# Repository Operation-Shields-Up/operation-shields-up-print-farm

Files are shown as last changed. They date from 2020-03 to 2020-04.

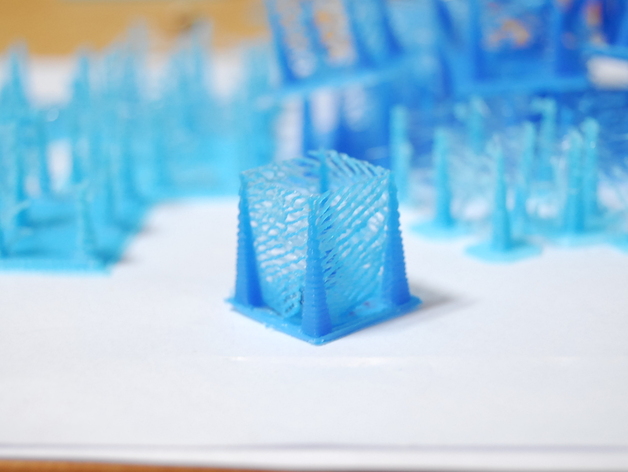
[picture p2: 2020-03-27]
models/calibration/Retraction_test_/images/cDSC_0050_preview_featured.jpg

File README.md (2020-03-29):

# Operation Shields UP

## GUIDES

- [Extrusion multiplier calibration](https://help.prusa3d.com/en/article/extrusion-multiplier-calibration_2257)

## FAQ

Q: What type of filament can I use?

A: We prefer PETG but will accept PLA.

Q: What settings should I use when I slice the models?

A: We are using a .2 mm layer height and a infill of 45% or more.

Q: Will the models change?

A: Likely, please follow the repo and we will update the files as we adopt new versions.
   We are actively working with PRUSA helping to vet the designs and integrate them with 
   our process and other components.

Q: How do I get in contact with you?

A: Reach us through our website [https://www.opshieldsup.org](https://www.opshieldsup.org)

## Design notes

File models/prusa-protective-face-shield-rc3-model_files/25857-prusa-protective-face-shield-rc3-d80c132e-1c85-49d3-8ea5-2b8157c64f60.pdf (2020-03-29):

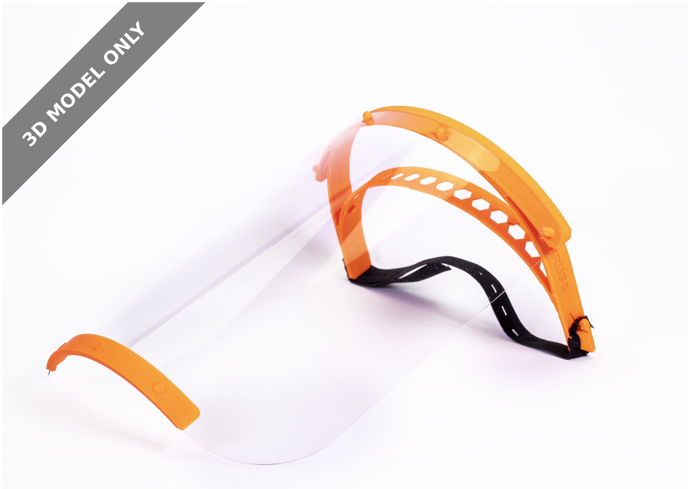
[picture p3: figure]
3D MODEL ONLY

## Summary

A prototype face shield that we developed. In three days, we went through dozens of prototypes and two verifications with the Czech Ministry of Health.

Check this print (https://www.prusaprinters.org/prints/27267) for 2 and 4 stack versions.

Version RC3 changelog Changes from RC2:

Removed hexagonal holes for faster printing speeds
With faster printing we use on our farm, some pieces had sharp points and based on testing, the venting is not needed as much Several optimizations for stack printing
New print files with 4 headbands stacked (https://www.prusaprinters.org/prints/27267) on top of each other Stacking headbands is a great idea by the community, especially useful for overnight printing

Prusa Research (https://www.prusaprinters.org/social/16/prints)

## Prusa Protective Face Shield - RC3

VIEW IN BROWSER (https://www.prusaprinters.org/prints/25857-prusa-protective-face-shield-rc3)

updated 27. 3. 2020 | published 26. 3. 2020

•
◦

•
•
◦

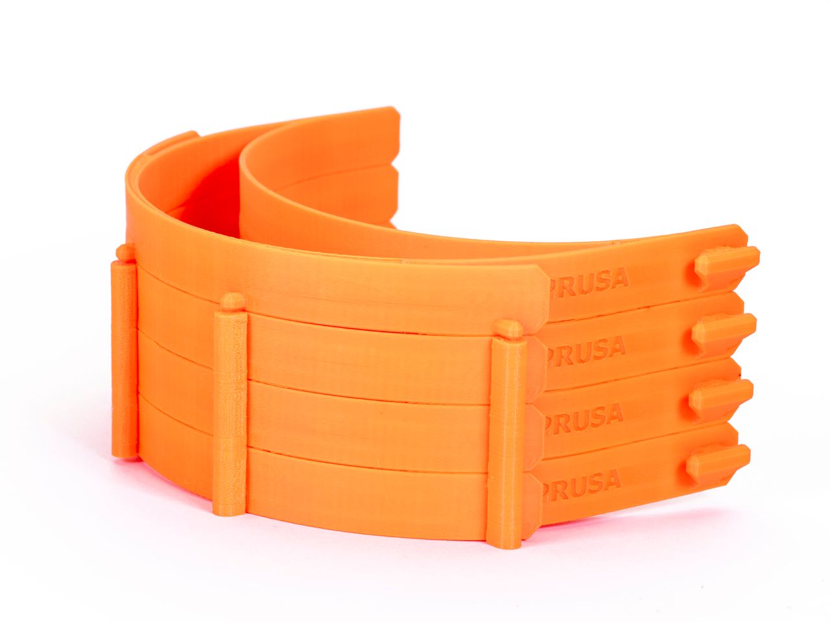
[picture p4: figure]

Version RC2 Changes from RC1:

Increased wall thickness (slightly stiffer and more durable)
Inner wall from 1.5 mm to 2 mm
Outer wall from 2 mm to 2.5 mm
The headband is no longer printed compressed - Lower pressure on the temple
The visor was moved further away from the forehead - This allows a better fit over bigger respirators and protective goggles
The printed part now has an extension for the visor (the visor curves less than the headband).

For now, both RC1 and RC2 versions are relevant. RC1 lets you fit more printed parts on a single print bed. However, if maximum yield isn’t the priority, RC2 provides slightly better protection and is more comfortable to

•
◦
◦
•

•

•

wear.

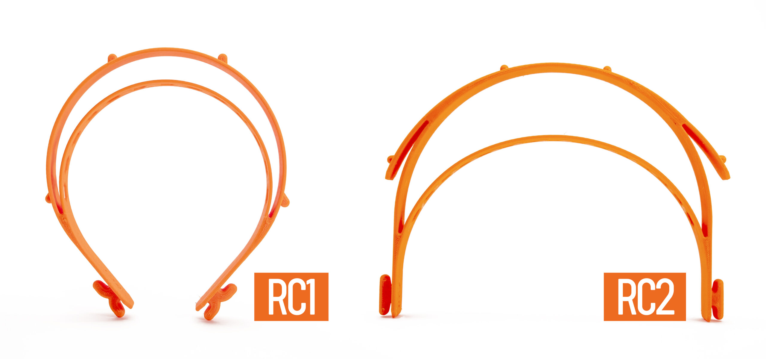
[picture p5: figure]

If you want to manufacture shields for others PLEASE READ THIS CAREFULLY

Act as if you were infected by the COVID-19 virus. Wear a face mask and a fresh pair of gloves when collecting each batch of printed parts. Store the parts immediately in a sealable bag.
Talk with whoever you’re making the shields for, let them know about your manufacturing environment
There is still debate about how long the virus survives on plastic, but most sources mention 2-3 days. That means that by letting the packed face shields sit for 2-3 days before distributing them, you’ll greatly reduce risk of transmission
Do not store the entire stock in one place, minimize the risk of cross contamination

More information: https://blog.prusaprinters.org/from-design-to-mass-3d-printing-of-medical-shields-in-three-days/ (https://blog.prusaprinters.org/from-design-to-mass-3d-printing-of-medical-shields-in-three-days/)

How to STERILIZE the face shields Sterilization guide (https://help.prusa3d.com/en/article/prusa-face-shield-disinfection_125457) We have tests with live COVID running to verify as many of these sterilization methods as possible.

Assembly manual: English version (https://manual.prusa3d.com/Guide/Prusa+Face+Shield/1527) English Community version using a laminating foil (https://manual.prusa3d.com/Guide/Assembling+the+Prusa+Face+Shield+-+community+version/1528#s41280) Czech version (https://manual.prusa3d.com/Guide/Prusa+Oblicejovy+Stit/1526)

Video:

"https://www.youtube.com/embed/pP7z3iw76GA"

Rubber band You can either use a thicker one and make a hole in it at each end (make at least 10 mm cut) or use a thin one and tie it to both ends of the shield.

•

•

•

•

Model Files (.stl, .3mf, .obj, .amf) | DOWNLOAD ALL FILES (https://www.prusaprinters.org/prints/25857-prusa-protective-face-shield-rc3/files)

354.1 KB
updated 26. 3. 2020 | (https://www.prusaprinters.org/prints/25857-prusa-protective-face-shield-rc3/files)

729.6 KB
updated 26. 3. 2020 | (https://www.prusaprinters.org/prints/25857-prusa-protective-face-shield-rc3/files)

873.8 KB
updated 26. 3. 2020 | (https://www.prusaprinters.org/prints/25857-prusa-protective-face-shield-rc3/files)

Visor / front plate

there is a DXF drawing in the file section (and an alternative longer version)
the holes can be made with a standard office hole puncher
we used 0.5 mm thick petg sheet (Covestro VIVAK), but you should be able to use any clear laser cuttable plastic with similar thickness.

Visor PDF drawings Normal size (http://prusa3d.com/downloads/others/COVID19_SHIELD_FOIL.pdf) Extended version (dentists) (http://prusa3d.com/downloads/others/COVID19_SHIELD_FOIL_LONG.pdf)

Licence and selling of face shields We share these files under non-commercial licence. It would be great if you donated these shields to those in need for free. If you need to cover your production costs, we are ok with you selling the shields for production cost. However, we do not want to see these shields on eBay for $50.

Healthcare (https://www.prusaprinters.org/prints?categoryId=87) > Accessibility (https://www.prusaprinters.org/prints?categoryId=88)

Supports are not necessary. Print with at least 3 perimeters, about 30% infill.

Ideally, print it from PETG.

•

•
•

covid19_headband_rc3_1pcs.3mf

covid19_headband_rc3.stl

covid19_headband_rc3.stp

290.5 KB
updated 27. 3. 2020 | (https://www.prusaprinters.org/prints/25857-prusa-protective-face-shield-rc3/files)

287.6 KB
updated 27. 3. 2020 | (https://www.prusaprinters.org/prints/25857-prusa-protective-face-shield-rc3/files)

662.6 KB
updated 27. 3. 2020 | (https://www.prusaprinters.org/prints/25857-prusa-protective-face-shield-rc3/files)

975.6 KB
updated 27. 3. 2020 | (https://www.prusaprinters.org/prints/25857-prusa-protective-face-shield-rc3/files)

284.2 KB
updated 27. 3. 2020 | (https://www.prusaprinters.org/prints/25857-prusa-protective-face-shield-rc3/files)

585.1 KB
updated 27. 3. 2020 | (https://www.prusaprinters.org/prints/25857-prusa-protective-face-shield-rc3/files)

841.8 KB
updated 27. 3. 2020 | (https://www.prusaprinters.org/prints/25857-prusa-protective-face-shield-rc3/files)

383.1 KB
updated 27. 3. 2020 | (https://www.prusaprinters.org/prints/25857-prusa-protective-face-shield-rc3/files)

321.6 KB
updated 27. 3. 2020 | (https://www.prusaprinters.org/prints/25857-prusa-protective-face-shield-rc3/files)

covid19_headband_rc2_1pcs.3mf

covid19_headband_rc2_2pcs.3mf

covid19_headband_rc2.stl

covid19_shield_rc2.stp

covid19-shield.3mf

covid19_headband_rc1.stl

covid19_shiled_r1.stp

bottom_reinforcement.stl

bottom_reinforcement.step

3.8 KB
updated 27. 3. 2020 | (https://www.prusaprinters.org/prints/25857-prusa-protective-face-shield-rc3/files)

300.2 KB
updated 27. 3. 2020 | (https://www.prusaprinters.org/prints/25857-prusa-protective-face-shield-rc3/files)
- The Author has not uploaded any print files. Try to search in User print files (https://www.prusaprinters.org/prints/25857-prusa-protective-face-shield-rc3/user-gcodes) section or generate and upload your own.

## License

This work is licensed under a
Creative Commons (4.0 International License)

Attribution-NonCommercial (http://creativecommons.org/licenses/by-nc/4.0/)

✖ | Sharing without ATTRIBUTION
✔ | Remix Culture allowed
✖ | Commercial Use
✖ | Free Cultural Works
✖ | Meets Open Definition

shield_final.dxf

shield_longer_version.dxf

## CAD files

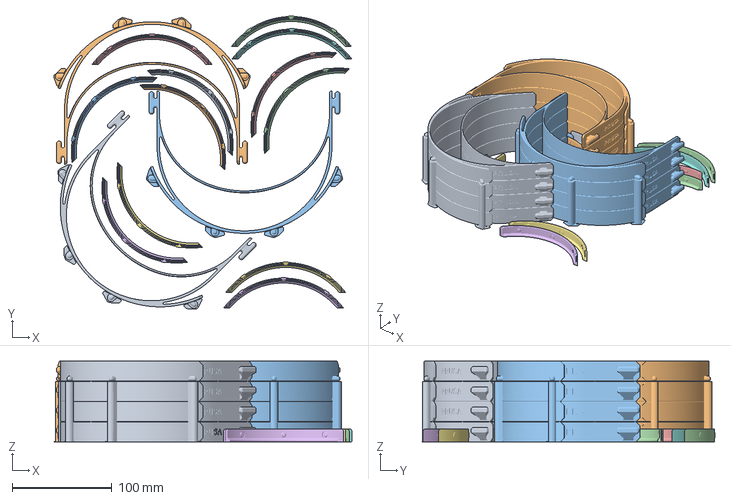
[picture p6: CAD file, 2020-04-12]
gcode/artillery/sidewinder/PRUSA_TOP_STACK_AND_BOTTOMS.3mf
298.0 x 293.1 x 80.8 mm
covid19_headband_quadro_rc31.stl
bottom_reinforcement.stl

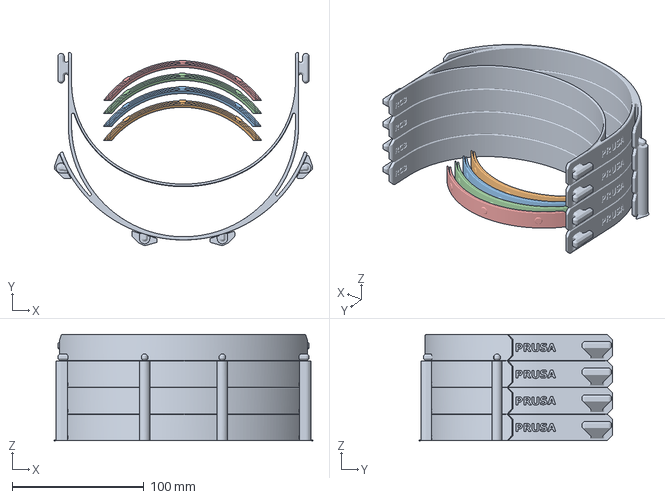
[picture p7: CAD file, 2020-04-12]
gcode/creality/ender_3/PRUSA_TOP_STACK_AND_BOTTOMS.3mf
196.0 x 146.8 x 80.8 mm
covid19_headband_quadro_rc31.stl
bottom_reinforcement.stl

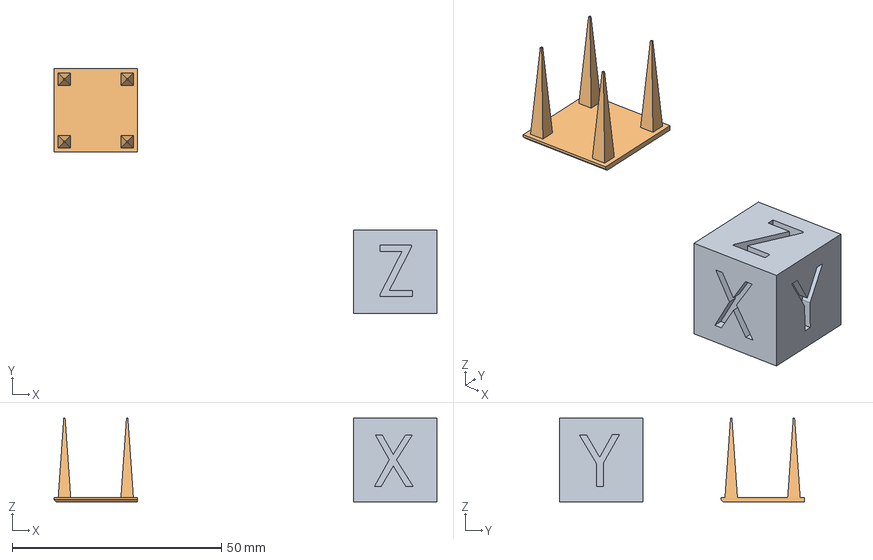
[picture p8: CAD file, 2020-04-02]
gcode/flsun/qq-s/CALIBRATION_TEST.3mf
91.6 x 58.5 x 20.0 mm

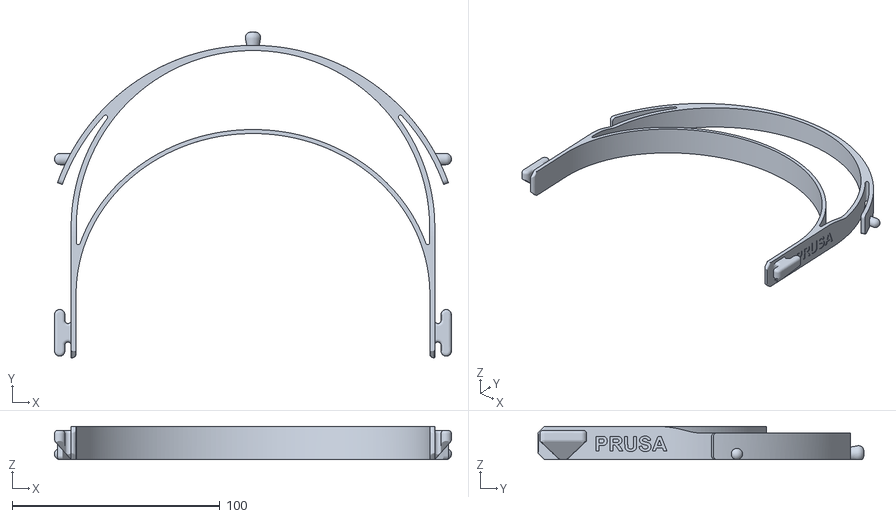
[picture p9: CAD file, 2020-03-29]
models/3_5/covid19_headband_3.5_branded.stl
191.0 x 156.7 x 16.0

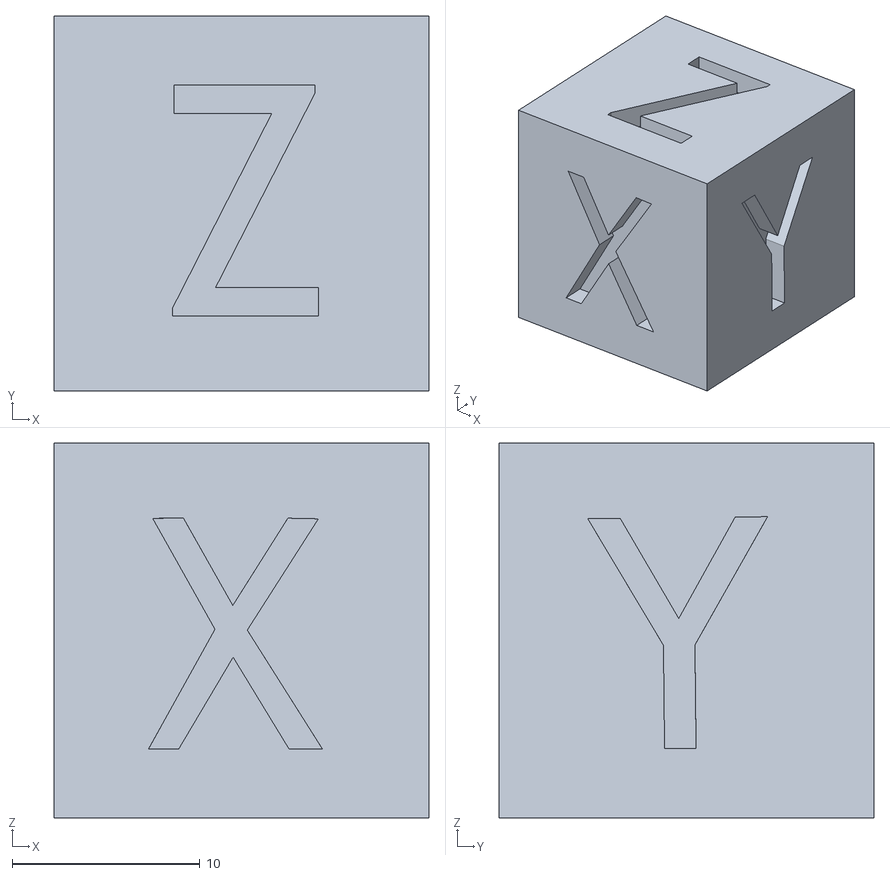
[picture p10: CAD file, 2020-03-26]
models/calibration/XYZ_20mm_Calibration_Cube/files/xyzCalibration_cube.stl
20.0 x 20.0 x 20.0

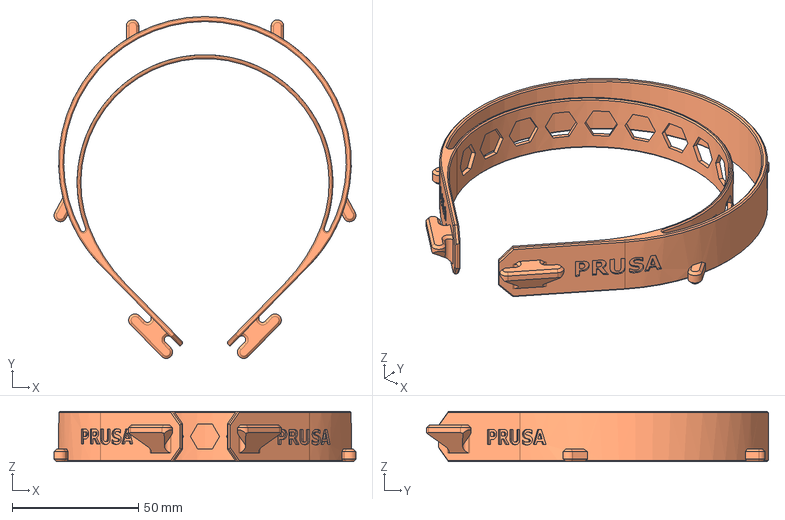
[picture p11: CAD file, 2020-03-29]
models/prusa-protective-face-shield-rc3-model_files/covid19_shiled_r1.stp
119.7 x 135.6 x 20.0 mm

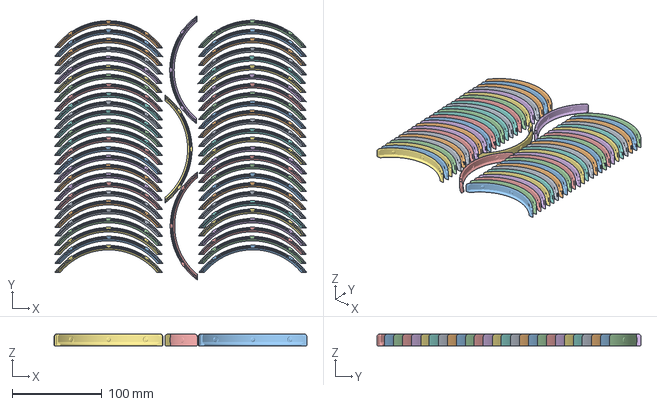
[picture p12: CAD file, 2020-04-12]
gcode/artillery/sidewinder/PRUSA_BOTTOM_PLATE.3mf
281.0 x 293.6 x 13.0 mm

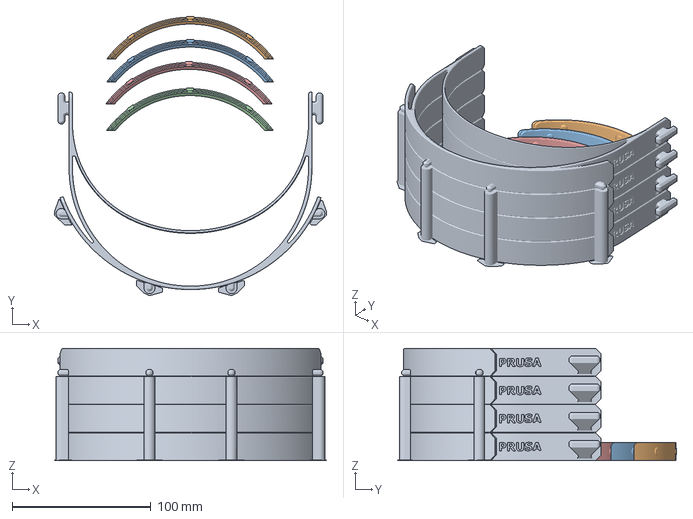
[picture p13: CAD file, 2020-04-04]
gcode/creality/ender_3/PRUSA_QUAD_STACK_WITH_BOTTOM.3mf
196.0 x 201.0 x 80.8 mm
covid19_headband_quadro_rc31.stl
bottom_reinforcement.stl

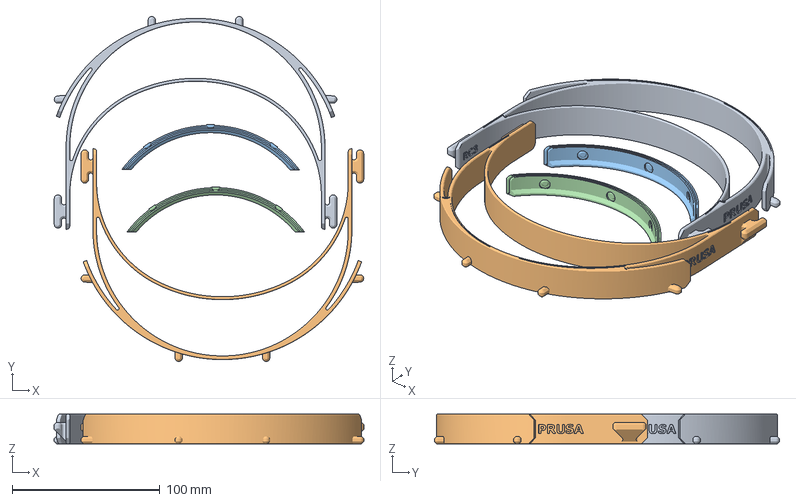
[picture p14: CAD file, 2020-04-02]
gcode/flsun/qq-s/PRUSA_FACE_SHIELD.3mf
209.2 x 233.1 x 20.0 mm

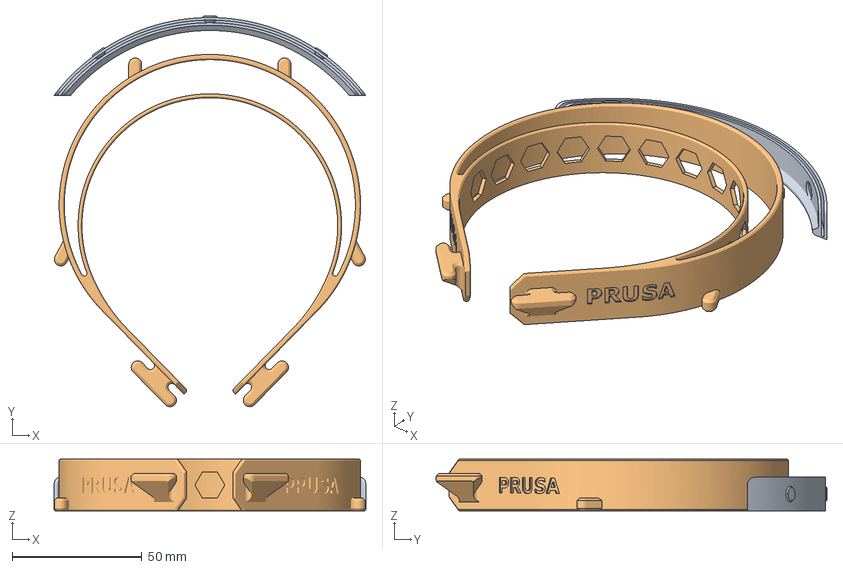
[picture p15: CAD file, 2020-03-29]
models/prusa-protective-face-shield-rc3-model_files/covid19-shield.3mf
120.1 x 150.3 x 20.0 mm
reinforcement_final.stl
COVID19_SHILED_R1 (1).stl

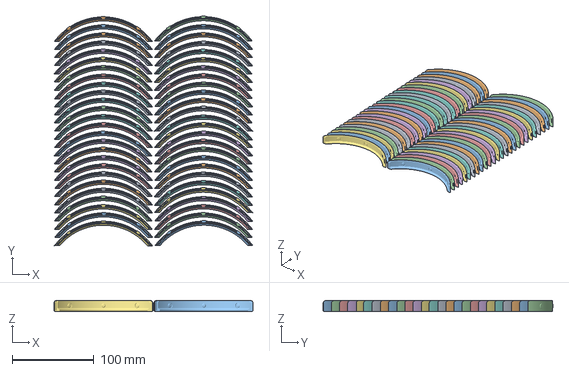
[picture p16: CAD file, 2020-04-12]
gcode/artillery/sidewinder/PRUSA_BOTTOM_PLATE_PARTIAL.3mf
243.4 x 280.8 x 13.0 mm

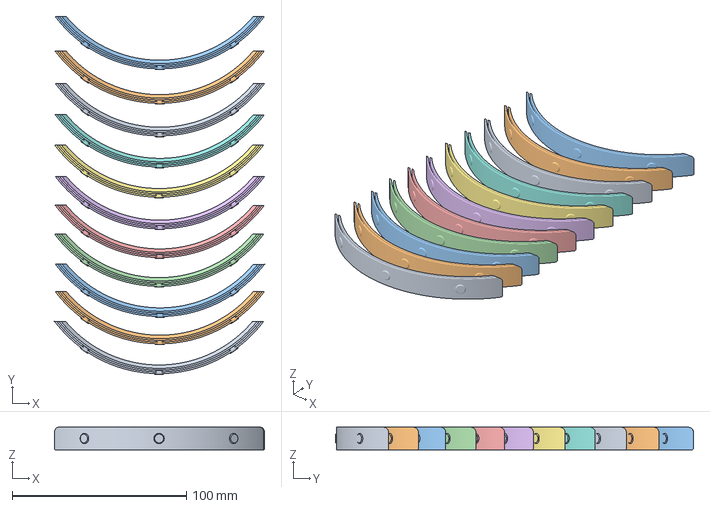
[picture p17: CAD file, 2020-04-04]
gcode/creality/ender_3/PRUSA_BOTTOM_PLATE_HALF_COUNT.3mf
120.5 x 205.5 x 13.0 mm

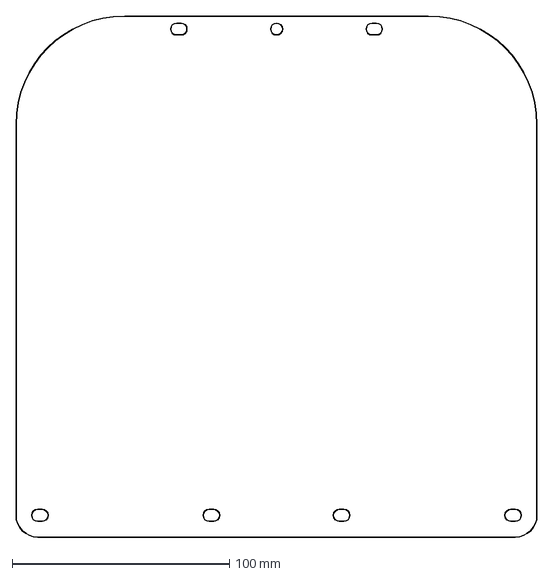
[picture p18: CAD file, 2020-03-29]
models/prusa-protective-face-shield-rc3-model_files/shield_final.dxf
240.0 x 240.0 mm

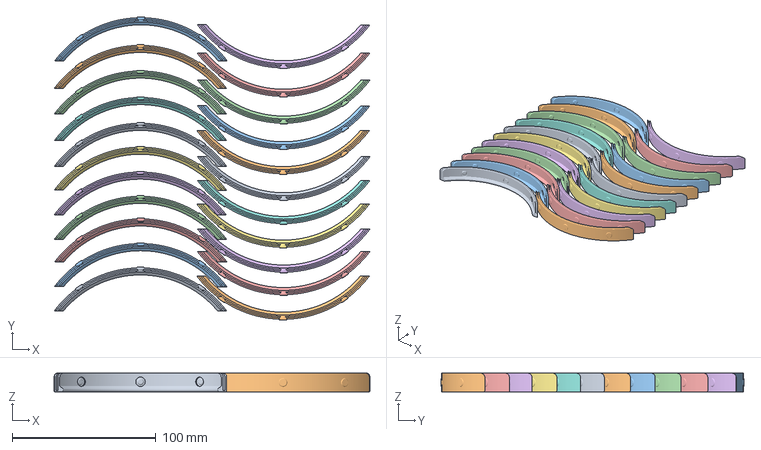
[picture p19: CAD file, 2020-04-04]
gcode/creality/ender_3/PRUSA_BOTTOM_PLATE.3mf
219.9 x 210.9 x 13.0 mm

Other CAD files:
models/prusa-protective-face-shield-rc3-model_files/bottom_reinforcement.step
models/prusa-protective-face-shield-rc3-model_files/covid19_headband_rc1.stl
models/prusa-protective-face-shield-rc3-model_files/covid19_headband_rc3.stl
models/prusa-protective-face-shield-rc3-model_files/covid19_headband_rc3_1pcs.3mf
models/prusa-protective-face-shield-rc3-model_files/bottom_reinforcement.stl
models/prusa-protective-face-shield-rc3-model_files/covid19_headband_rc2.stl
models/prusa-protective-face-shield-rc3-model_files/covid19_headband_rc3.stp
models/prusa-protective-face-shield-rc3-model_files/covid19_shield_rc2.stp
models/prusa-protective-face-shield-rc3-model_files/prusa_protective_face_shield_cover_rc1 v1.stl

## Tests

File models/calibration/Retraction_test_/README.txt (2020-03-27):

                   .:                     :,                                          
,:::::::: ::`      :::                   :::                                          
,:::::::: ::`      :::                   :::                                          
.,,:::,,, ::`.:,   ... .. .:,     .:. ..`... ..`   ..   .:,    .. ::  .::,     .:,`   
   ,::    :::::::  ::, :::::::  `:::::::.,:: :::  ::: .::::::  ::::: ::::::  .::::::  
   ,::    :::::::: ::, :::::::: ::::::::.,:: :::  ::: :::,:::, ::::: ::::::, :::::::: 
   ,::    :::  ::: ::, :::  :::`::.  :::.,::  ::,`::`:::   ::: :::  `::,`   :::   ::: 
   ,::    ::.  ::: ::, ::`  :::.::    ::.,::  :::::: ::::::::: ::`   :::::: ::::::::: 
   ,::    ::.  ::: ::, ::`  :::.::    ::.,::  .::::: ::::::::: ::`    ::::::::::::::: 
   ,::    ::.  ::: ::, ::`  ::: ::: `:::.,::   ::::  :::`  ,,, ::`  .::  :::.::.  ,,, 
   ,::    ::.  ::: ::, ::`  ::: ::::::::.,::   ::::   :::::::` ::`   ::::::: :::::::. 
   ,::    ::.  ::: ::, ::`  :::  :::::::`,::    ::.    :::::`  ::`   ::::::   :::::.  
                                ::,  ,::                               ``             
                                ::::::::                                              
                                 ::::::                                               
                                  `,,`

https://www.thingiverse.com/thing:909901
Retraction test  by deltapenguin is licensed under the GNU - GPL license.
http://creativecommons.org/licenses/GPL/2.0/

# Summary

(10/19/2016)
I did retraction calibration for B'struder.

Extruder drive: B’struder
Kysan Nema 17 5.18:1 geared stepper motor, 2.4 V, 1.0 A

config.g of RepRapFirmware-dc42 1.12a

M92 411.230
M201 X4000 Y4000 Z4000 E3000 ; Accelerations (mm/s^2)
M203 X15000 Y15000 Z15000 E15000 ; Maximum speeds (mm/min)
M906 X800 Y800 Z800 E800 ; Set motor currents (mA)
M92 411.230

Retraction setting in Slic3r 1.2.9:
Length: 3.4 mm
Z Lift: 0.4 mm
Speed: 15 mm/s (10 mm/s and 20 mm/s give similar result.)
Retraction after layer change: on
Wipe on retraction: on

Filament: eSun PLA 1.75 mm
Layer height: 0.2 mm 
Printing speed: 20 mm/s
Travel speed: 250 mm/s

190 degrees Celsius gave better result than 180 degrees Celsius. Why?!
(3/16/2016)

White one was done by RepRapPro Fisher last year.
There was huge improvement in retraction quality. 
Only modification I did I glued end of Bowden tube on the push fitting of the extruder half year ago. 

190 C or 180C wouldn't make much difference. 

Slic3r settings (3/16/2016):
Layer height: 0.25 mm
Travel speed: 200 mm/s

Retraction
Length: 2 mm
Lift Z: 0.4 mm
Speed: 40 mm/s
Minimum travel after retraction: 2 mm
Retract on layer change: on 
Wipe while retracting: on

Previous Slic3r settings (2015):  
Layer height; 0.1 mm  
Extrusion width: 0.28 mm  
Printing speed: 30 mm/s  
Travel speed: 20 mm/s  
Retraction   
Length: 4.5 mm  
Lift Z: 0.075 mm  
Speed: 150 mm/s  
Extra length on restart: 0.1 mm  

Source:  
Fine Positive Features Performance  
http://www.thingiverse.com/download:872736

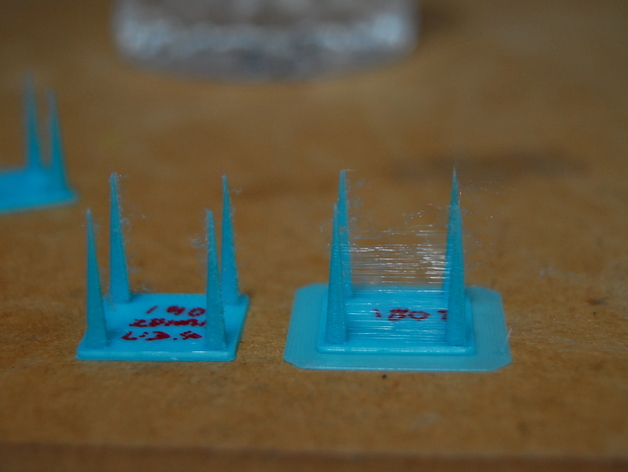
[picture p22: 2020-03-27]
models/calibration/Retraction_test_/images/8e2b50c404c6165361cde9ecc9c02d9c_preview_featured.jpg

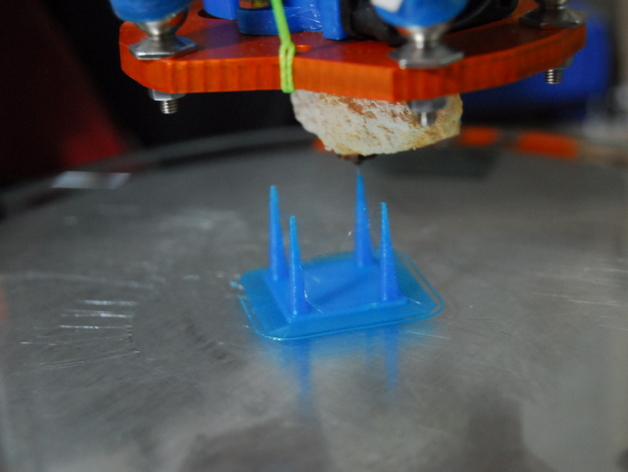
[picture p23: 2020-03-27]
models/calibration/Retraction_test_/images/1a86d2e71341b225d7d05007d84f7ea7_preview_featured.jpg

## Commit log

2020-03-26 Added models
    [bottom_reinforcement.stl, covid19_headband_3.5_branded.stl, covid19_headband_rc2.stl]
2020-03-26 Remove old version
    [covid19_headband_rc2.stl]
2020-03-26 add calibration file
    [xyzCalibration_cube.stl]
2020-03-27 Added gcode for the new ender 3 pros that arrived today and more calibration models to use for setup
    [four_square_cons.stl]
2020-03-28 Adding some slices to test prusaslicer vs cura to resolve issues
    [CALIBRATION_CUBE_ENDER3.3mf, PRUSA_TOP_BAND_ENDER3.3mf]
2020-03-28 Netfab repair of surface mesh
    [covid19_headband_3.5_branded.stl]
2020-03-29 Added Prusa RC3 models
    [bottom_reinforcement.step, bottom_reinforcement.stl, covid19-shield.3mf, covid19_headband_rc1.stl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]
2020-04-02 Add gcode and files contributed by members
    [CALIBRATION_TEST.3mf, PRUSA_FACE_SHIELD.3mf]
2020-04-04 Added latest Ender 3 profiles and slices for .8mm nozzles
    [CALIBRATION_CUBE_ENDER3.3mf, PRUSA_BOTTOM_PLATE.3mf, PRUSA_BOTTOM_PLATE_HALF_COUNT.3mf, PRUSA_QUAD_STACK_WITH_BOTTOM.3mf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]
2020-04-04 Added stacked model
    [covid19_headband_quadro_rc31.stl]
2020-04-07 Added more gcode
    [bottom_reinforcement.3mf]
2020-04-08 removed old versions
    [bottom_reinforcement.3mf]
2020-04-12 updated gcode files
    [PRUSA_BOTTOM_PLATE.3mf, PRUSA_BOTTOM_PLATE_PARTIAL.3mf, PRUSA_TOP_STACK_AND_BOTTOMS.3mf]
